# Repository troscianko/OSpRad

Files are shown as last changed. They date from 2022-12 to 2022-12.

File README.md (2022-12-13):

# OSpRad
## An open-source, low-cost, high-sensitivity spectroradiometer

Developed by Jolyon Troscianko - 2022

Released under GPL-3.0 license.

This project allows users to build their own low-cost, high-sensitivity spectroradiometer for measuring radiance/irradiance based on the Hamamatsu C12880MA chip. The spectral range of ~310 to 880nm and resoltuion of ~9nm make the OSpRad particularly well suited to visual modelling.

Testing shows that the system can measure spectral radiance down to around 0.001 cd/sqm, and irradiance down to around 0.005 lx.

Included in this project are the 3D STL files for creating your own housing, code for uploading to an arduino nano microcontroller, and a Python app for interfacing with the OSpRad spectroradiometer via desktop computer or Android smartphone (via Pydroid 3).

Code and data are released without any form of warranty, and the author accepts no liability.

## User interface app
OSpRad units are controlled through the included graphical user interface. This is written in Python 3, and can run from desktop computers (currently Linux) or Android smartphones (requires Pydroid 3 app). Simply plug in the OSpRad via USB and run this code to launch the app. The OSpRad communicates via serial connection and the USB also provides power. The app has a few dependences in Python: tkinter, matplotlib, serial, (and for Android) usb4a and usbserial4a. Calibration data for the OSpRad units must be provided by placing the calibration_data.csv file (with relevant data for each specific unit#) in the same directory as you're launching the code from. Spectral data are stored in data.csv in the same directory.


The app saves all relevant data, including calibrated watts/(sqm * nm) or watts/(sr * sqm * nm), raw count data, integration time, number of saturated photosites (to ensure measurement isn't over-exposed), number of scans averaged, time and date of the the measurement, and a label if one was chosen.

Repeat measurements can be made by ticking the relevant checkbox (for data logging), specify whether to measure radiance, irradiance, or both, and the frequency (in seconds).

## App running from smart phone
To run from an Android phone, install Pydroid 3, use pip to install the dependences (this requires an additional app, just follow the on-screen instructions). Then connect the phone to the OSpRad and run the code. Ensure the calibration_data.csv file is in the same directory as this python code. Most modern phones have a USB-C port, so you'll need a USB-C to USB-A (female receptacle). Which is a standard cable. Older phones with a USB-micro port require a USB-micro OTG to USB-mini cable (less common, but easy to buy online).


# Construction
## Parts list:
- Hamamatsu C12880MA chip
- 3D printed components (black PLA or ABS recommended, not PET due to IR transparency)
- Arduino Nano
- Cosine corrector: 8mm diameter, 0.5mm thick virgin PTFE sheet, sanded in circular motion with 180 grit paper
- Digital micro servo (Savox – SH-0256 recommended)
- USB cable(s) for mobile phone. e.g. USB-C to USB-A female, and USB-A male to USB-mini
- Solder and cables (e.g. strip the cables from an old Ethernet cable, 10cm lengths)
- UV curing glue (or similar, for gluing the PTFE diffuser to the shutter wheel)
- Optional physical protection: Circular fused silica microscope cover-slip or UV-transmitting PMMA disk

The 3D printed parts will need some filing/sanding/drilling to get a snug fit between the housing and shutter wheel. File down the outside of the shutter wheel shaft to give it a smooth, circular cross-section (i.e. remove 3D printing imperfections). Then use a circular file to enlarge the hole in the housing until the two fit together snugly and the shaft rotates smoothly without play. The centre of the shutter wheel shaft might need to be enlarged slightly with a 4mm drill bit to get the screw head down inside it. To get a fit between the shutter wheel shaft and the servo, use a heat-gun or lighter flame to heat the end of the shaft, and push the two carefully together while the plastic is slightly flexible, ensuring it cools in the right angle. It will cool and harden in the correct shape, so that when screwed together it will have a nice grip.

## 3D printed parts:


Solder the parts together as shown below. Roughly 10cm lengths of wire should be good. Note the use of different 5v sources for the servo and spectrometer chip. This is because the VIN pin suffers a voltage drop (due to its protective diode) from the USB's 5v source, which isn't quite high enough for stable spectrometer functioning.

## Circuit Diagram:
Circuit Diagram

## Arduino code
Use Arduino IDE to flash the firmware code to the Arduino Nano. There are four numbers in the code that you'll need to change in the supplied code (shown in comments at the top of the script). This is the ID of the unit (each unit needs its own ID so it can look up its calibration data) and the shutter wheel positions that correspond to "closed", "radiance" and "irradiance" measurement positions. Once you've flashed the code to the Arduino you can make a serial connection link within Arduino IDE (baud rate 115200) and send "w90" to the OSpRad. This will move the servo to its central position. Now it's in this position, remove the shutter wheel from the servo and re-attach it in the nearest position to "closed" (central) as possible, to get it roughly into the correct place. Next, use the same wheel position function ("w" plus number) to work out the precise numbers associated with the three required positions. The script contains a range of examples and your numbers should be similar. Once you've found the positions, update the numbers in the Arduino code and re-flash the Arduino Nano. Now the shutter wheel will move to the correct positions.

# Calibration
Calibration data for each OSpRad unit are stored in calibration_data.csv, using tab delineation. The file takes the following format:



The first column stores the unit#. This is the ID given to each unit (flashed to the Arduino Nano, see above). Each unit requires four rows of calibration data

This includes:

## Wavelength calibration "wavCoef"
[six coefficients required] The coefficients for the equation matching each photosite to its peak wavelength sensitivity are provided by the manufacturer when you purchase the spectrometer chip.

## Linearisation data "linCoefs"
[two coefficients] This describes the non-linear relationship between raw photosite ADC count data and linear flux. I found this is described by the function:

c[linear] = c / ( a * ln(( c + 1 ) * b )  )

at each photosite. Where c is the raw count value, and a and b are coefficients.

Example of linearisation model fitting with linear x-axis:


and logged x-axis to show effects at very low count numbers:


You can either measure this yourself for unit-specific linearisation values, or use a template, they are all very similar.

## Spectral sensitivity calibration "radSens" and "irrSens"
[288 numbers each] This requires access to a calibrated light source (with known emission spectra). Measure that source with the OSpRad in radiance and irradiance modes. See the included calibration spreadsheet to see how spectral radiance and irradiance calibration data are created.

Alternatively, you could simply use the included data as a template, but this would cause some error as there are unit-specific spectral sensitivity differences:

## Spectral radiance sensitivity:


## Spectral irradiance sensitivity:


Note that unit "E" used a cosine corrector with a different construction, explaining its lower sensitivity.

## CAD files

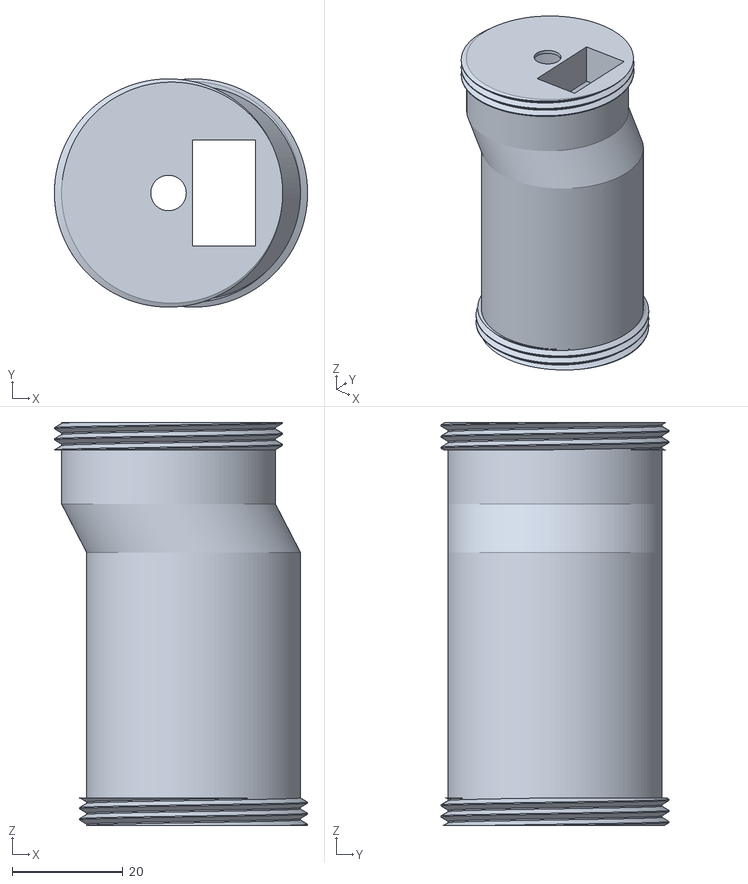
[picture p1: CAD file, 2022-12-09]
3D components/main_housing.stl
45.7 x 41.2 x 72.7

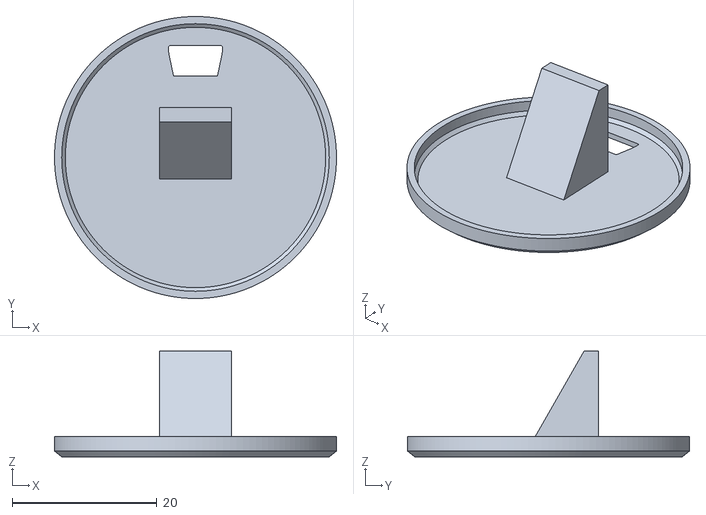
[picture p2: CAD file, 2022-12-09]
3D components/base_cap.stl
39.0 x 39.0 x 14.6

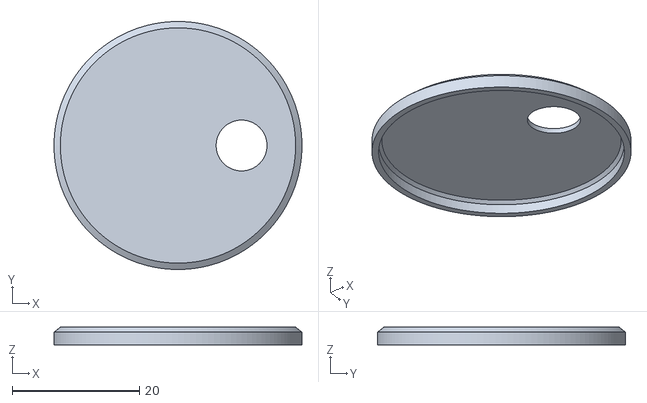
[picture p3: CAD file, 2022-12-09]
3D components/top_cap.stl
39.0 x 39.0 x 2.80

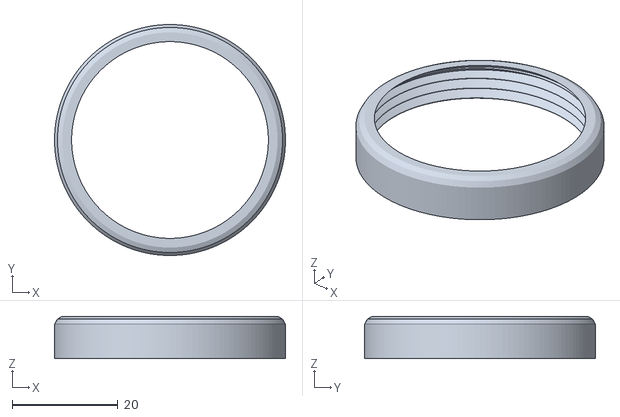
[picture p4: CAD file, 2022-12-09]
3D components/cap_tightenner.stl
43.6 x 43.6 x 8.01

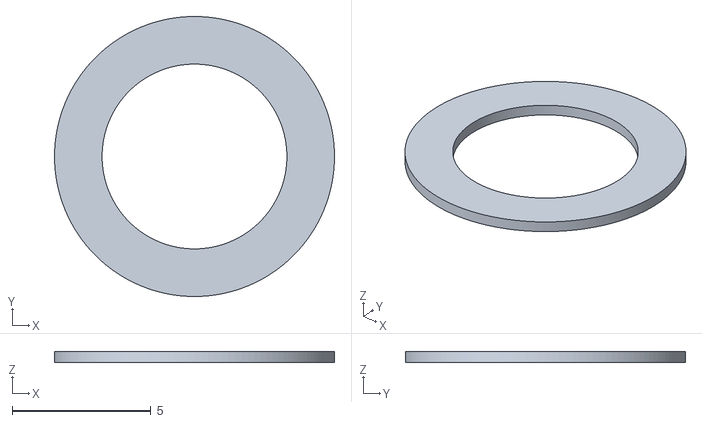
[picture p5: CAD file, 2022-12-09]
3D components/cosine_corrector_ring.stl
10.1 x 10.1 x 0.4

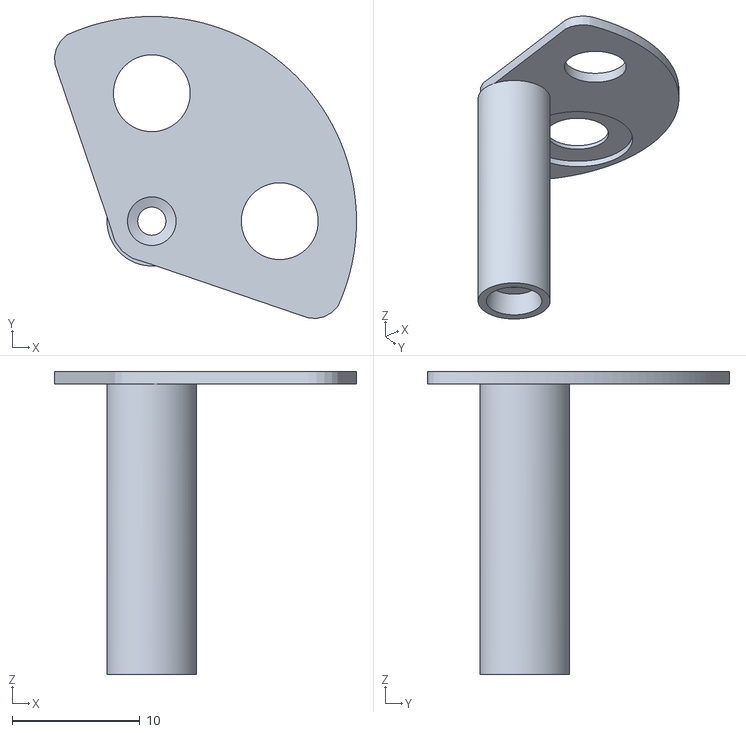
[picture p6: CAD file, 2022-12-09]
3D components/shutter_wheel.stl
23.6 x 23.6 x 23.7

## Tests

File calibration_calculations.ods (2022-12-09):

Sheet: wavelength
Input wavelength calibration data from manufacturer |  |  |  |  | Unit IDs used in the paper:
 |  |  |  |  | F | A | B | C | D | E
Unit# | 1 | 2 | 3 | 4 | 1.1 | 5 | 6 | 7 | 8 | 1.2
Chip# |  | 17L00450 | 17L00486 | 17L00452 |  | 22D04847 | 22D04848 | 22D04849 | 22D04850
A0 | 307.9260079 | 310.1909919 | 316.04777 | 316.437 | 307.9260079 | 308.811528062194 | 298.340179940819 | 305.619507434632 | 297.308340799761 | 307.9260079
B1 | 2.71E+00 | 2.708063 | 2.703318951 | 2.7107373 | 2.71E+00 | 2.72E+00 | 2.69E+00 | 2.69E+00 | 2.72E+00 | 2.71E+00
B2 | -1.42E-03 | -1.55E-03 | -1.53E-03 | -1.48E-03 | -1.42E-03 | -1.54E-03 | -6.74E-04 | -9.50E-04 | -1.15E-03 | -1.42E-03
B3 | -4.96E-06 | -4.14E-06 | -3.61E-06 | -4.86E-06 | -4.96E-06 | -4.61E-06 | -1.20E-05 | -8.96E-06 | -8.03E-06 | -4.96E-06
B4 | -1.67E-09 | -3.99E-09 | -7.24E-09 | -1.13E-09 | -1.67E-09 | -1.65E-09 | 2.67E-08 | 1.36E-08 | 1.24E-08 | -1.67E-09
B5 | 2.08E-11 | 2.33E-11 | 2.85E-11 | 1.88E-11 | 2.08E-11 | 1.931275476E-11 | -2.028818275E-11 | -8.8863563E-13 | -1.47806282E-12 | 2.08E-11
Wavelength resolution |  | 9.7 | 8.7 | 8.4 |  | 9 | 8.6 | 8.6 | 9
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

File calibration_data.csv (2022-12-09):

unit | data
1 | wavCoef | 307.9260079 | 2.707312092 | -0.00141580422 | -0.000004964305348 | -1.671093456E-09 | 2.079576302E-11
1 | radSens | 8860.39889268342 | 9481.20997548601 | 9810.77334662061 | 9920.39603187586 | 9894.7553398501 | 9773.35488985032 | 9521.13445309516 | 9359.4388262195 | 9267.580730103 | 9251.96351672845 | 9358.78793250297 | 9542.11317303258 | 9765.90823944888 | 10004.1907050279 | 10209.5320899131 | 10329.4231691733 | 10351.4847849311 | 10258.4255900929 | 10071.0288341834 | 9820.72888030758 | 9542.86231920622 | 9304.17081079018 | 9149.90689223668 | 9106.04237027336 | 9177.47086727677 | 9374.08634690858 | 9680.6437004329 | 10083.3295169321 | 10558.9231666401 | 11096.2535742206 | 11668.5130268139 | 12241.3137099973 | 12790.5152716533 | 13287.8068397276 | 13703.3206378967 | 14021.3253420803 | 14225.6751913229 | 14311.2019542275 | 14299.3867491586 | 14195.399288652 | 14038.6516448253 | 13849.6889242104 | 13657.7465520814 | 13489.3166461852 | 13351.3050988206 | 13264.9278367124 | 13224.8096692202 | 13253.7918910431 | 13364.1511132215 | 13504.3242427879 | 13708.0367556061 | 13967.4828538849 | 14264.6951938751 | 14583.5810995832 | 14913.0932301829 | 15250.2942593914 |
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

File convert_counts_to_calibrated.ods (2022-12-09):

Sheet: calibration data
Input wavelength calibration data from manufacturer
Unit# | 6
Chip# | 22D04848
A0 | 298.340179940819
B1 | 2.69E+00
B2 | -6.74E-04 |  | areas highlighted in grey require user-input
B3 | -1.20E-05
B4 | 2.67E-08
B5 | -2.028818275E-11
Wavelength resolution | 8.6
Filter | UV-PMMA filter 2mm
Linearisation coefficients
a | 0.12249
b | 3.258
 |  |  | Spectral sensitivities
pixel | wavelength | wavelength bins | radiance | irradiance
0 | 298.3 | 2.688686061287 | 5920.4770481686 | 1244.45273848688
1 | 301.0 | 2.68726739864201 | 6355.39171259082 | 1325.10198069419
2 | 303.7 | 2.68577771252501 | 6625.27590528988 | 1366.33384895208
3 | 306.4 | 2.68421763774398 | 6808.49588396844 | 1386.96314323333
4 | 309.1 | 2.68258780667503 | 6954.21666995321 | 1396.96420361701
5 | 311.8 | 2.68088884925601 | 7104.99510311891 | 1405.82919140519
6 | 314.4 | 2.67912139299199 | 7244.05994537217 | 1402.69222854897
7 | 317.1 | 2.67728606295401 | 7437.95455799429 | 1413.23992507994
8 | 319.8 | 2.675383481778 | 7697.88765171785 | 1439.8176698443
9 | 322.5 | 2.67341426966396 | 7916.3231501308 | 1458.8307447091
10 | 325.2 | 2.67137904438101 | 8104.91582593839 | 1477.12165821284
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
